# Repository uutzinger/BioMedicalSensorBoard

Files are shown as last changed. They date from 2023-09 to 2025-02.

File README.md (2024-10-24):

# MediBrick

A cost-effective Solution for Biomedical Measurements.

Urs Utzinger, 10/2024 and capstone teams: 24052 (2023/24), 23094 (2022/23).
Biomedical Engineering Department, The University of Arizona.

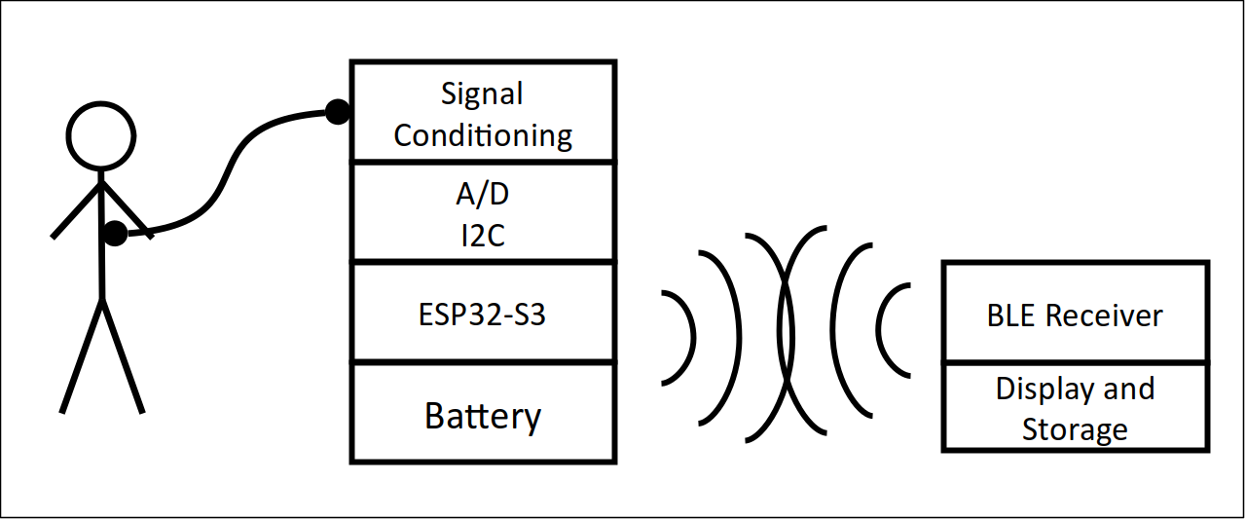
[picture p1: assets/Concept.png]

 
Table of Content:
<!-- TOC start (generated with https://github.com/derlin/bitdowntoc) -->

- [MediBrick](#medibrick)
   * [Problem Description](#problem-description)
   * [Project Goals](#project-goals)
   * [Measurement Solutions](#measurement-solutions)
   * [Microcontroller and Software](#microcontroller-and-software)
   * [Hardware](#hardware)
      + [Design and Manufacturing ](#design-and-manufacturing)
      + [Enclosures](#enclosures)
   * [Project Status](#project-status)

<!-- TOC end -->

<!-- TOC -->

Posters and Papers: 
- *Open source platform to measure physiological signals in a classroom setting*, BMES 2024 Annual Meeting: Biomedical Engineering Education - Poster Session C, Poster Q15 

## Problem Description

Biomedical engineering students need to practice measuring signals from living systems.
Measurement equipment is needed for classroom laboratories that can safely record common physiological parameters.
For a wide adoption, such equipment should be cost effective and repairable in-house.
Therefore, it should take advantage of existing components that are open source and distributed through domestic channels.
While there are commercial systems available [^fn1] [^fn2], there is no unifying approach that takes advantage of existing third party hardware, gives option to expand functionality at later time and uses open source software.  Such measurement modules could also be readily incorporated into academic research projects.

[^fn1]: Bioradio, https://staging.glneurotech.com/product-category/bioradio-all
[^fn2]: Protocentral https://protocentral.com

**An expandable, low-costs, open-design system is needed that measures physiological parameters in a class room setting in a safe manner.**

## Project Goals
- We strive to create an educational system to measure physiological signals.
- It shall be easily manufactured at an educational institution.
- It shall record, display and store common physiological measurements safely in a class room setting.

## Measurement Solutions
This project consists of the following measurement solutions:

| ECG and Impedance | Electronic Stethoscope and Blood Pressure | Pulse Oximeter | Temperature | Inertial Measurement Unit | Air Quality | Lung Capacity |
| --- | --- | --- | --- | --- | --- | --- |
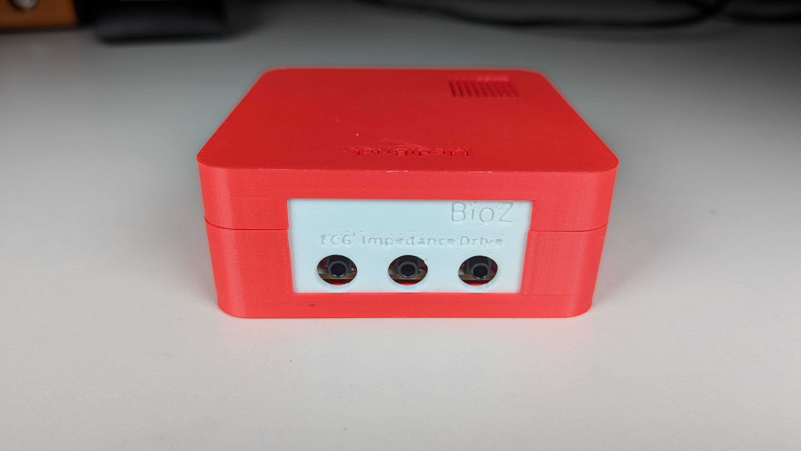
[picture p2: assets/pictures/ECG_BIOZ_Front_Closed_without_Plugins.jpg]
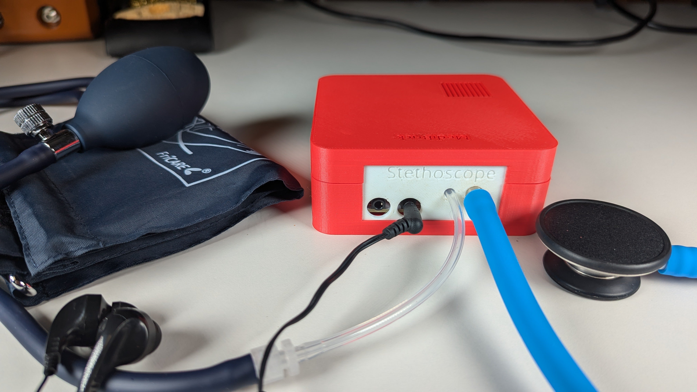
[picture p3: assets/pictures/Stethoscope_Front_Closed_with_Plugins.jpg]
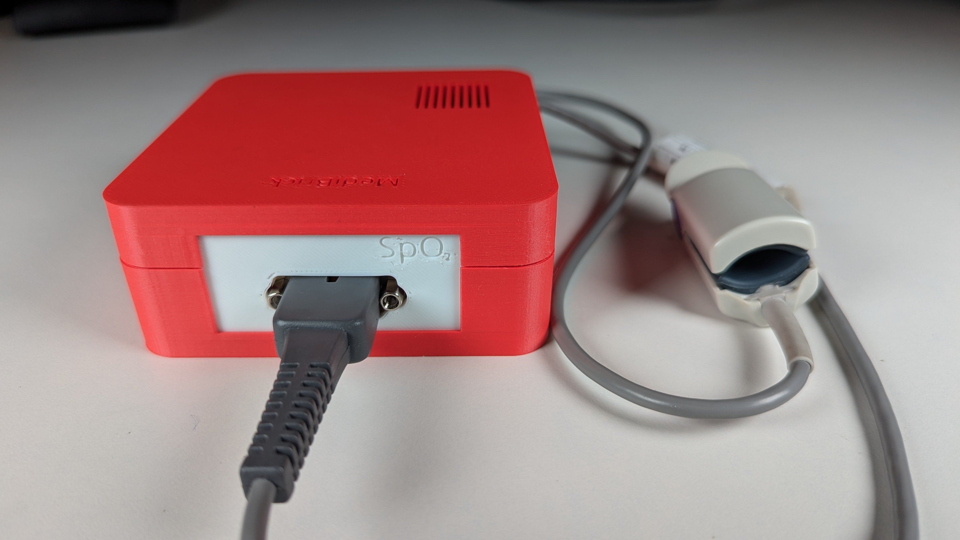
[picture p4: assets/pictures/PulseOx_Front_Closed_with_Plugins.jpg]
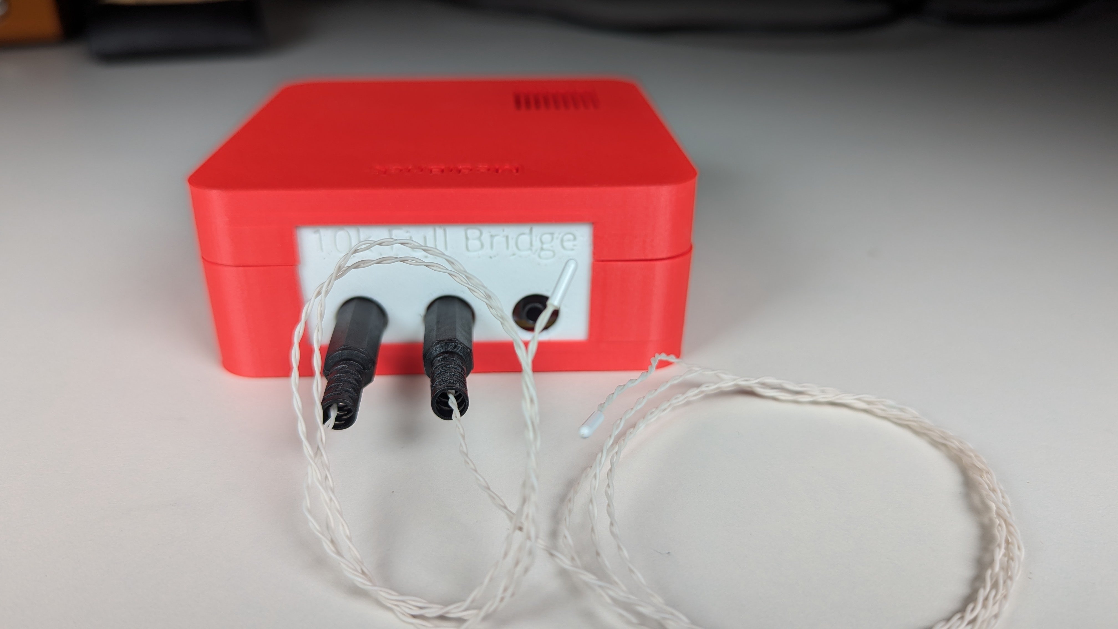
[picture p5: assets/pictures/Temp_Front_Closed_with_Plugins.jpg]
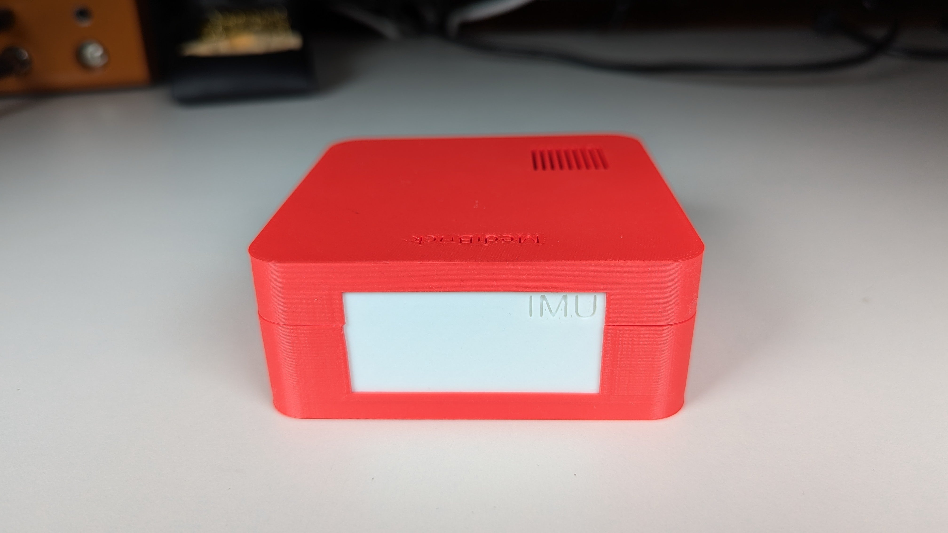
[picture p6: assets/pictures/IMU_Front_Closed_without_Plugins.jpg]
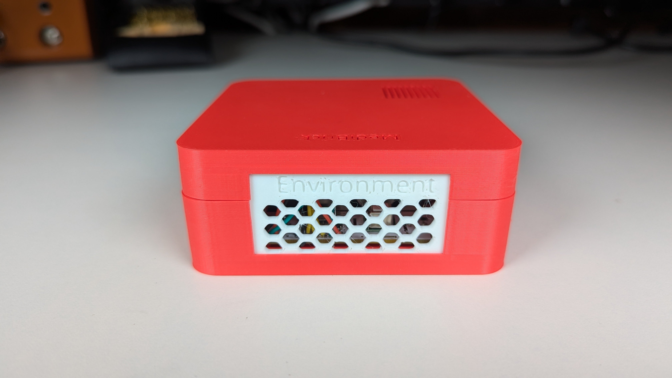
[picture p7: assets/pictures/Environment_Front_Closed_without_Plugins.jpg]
|  |  |  |  |  |  | N.A. |
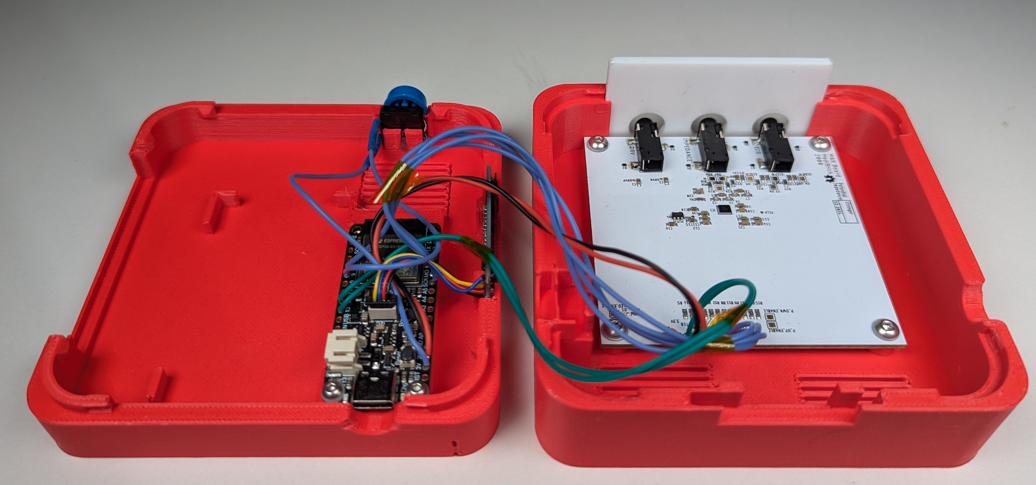
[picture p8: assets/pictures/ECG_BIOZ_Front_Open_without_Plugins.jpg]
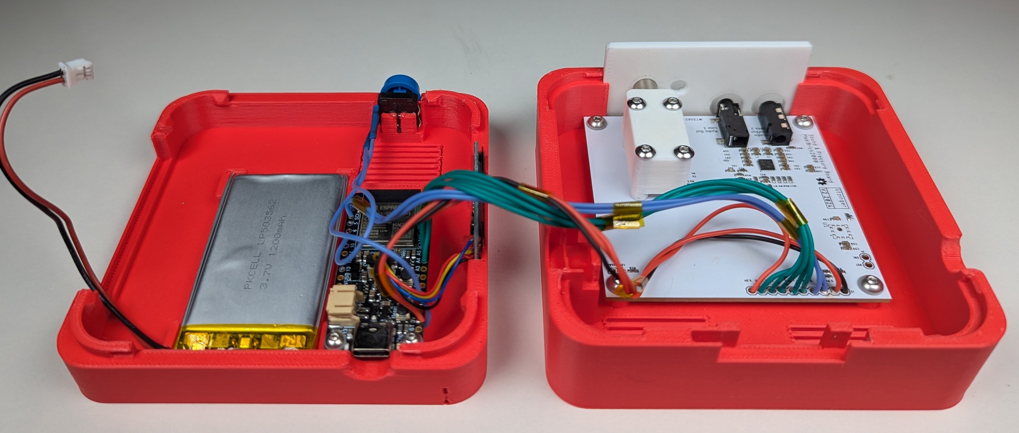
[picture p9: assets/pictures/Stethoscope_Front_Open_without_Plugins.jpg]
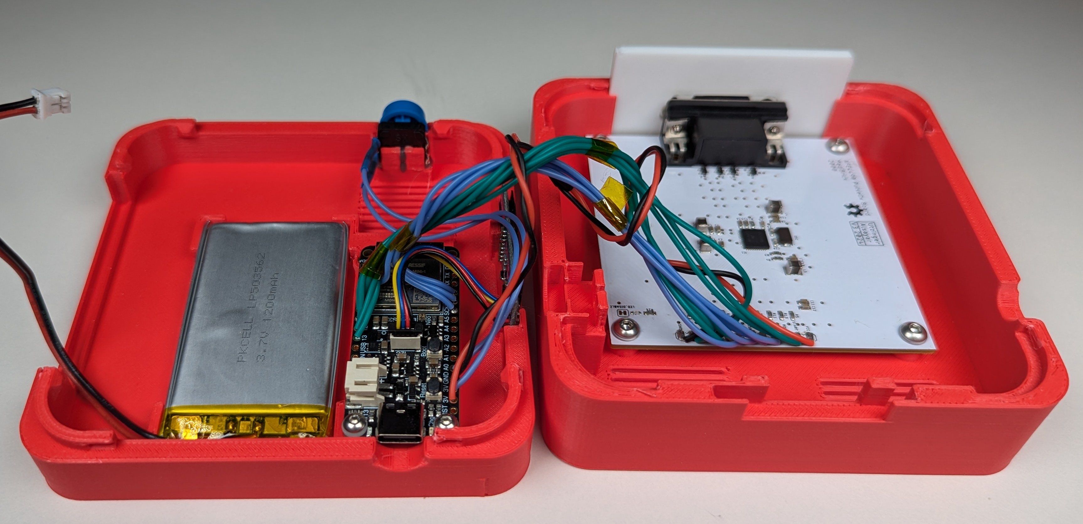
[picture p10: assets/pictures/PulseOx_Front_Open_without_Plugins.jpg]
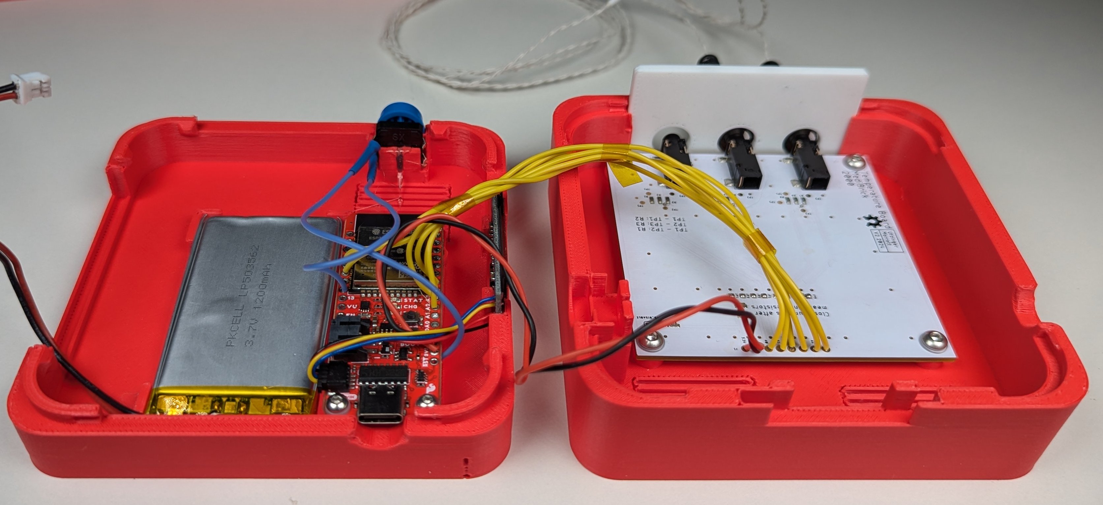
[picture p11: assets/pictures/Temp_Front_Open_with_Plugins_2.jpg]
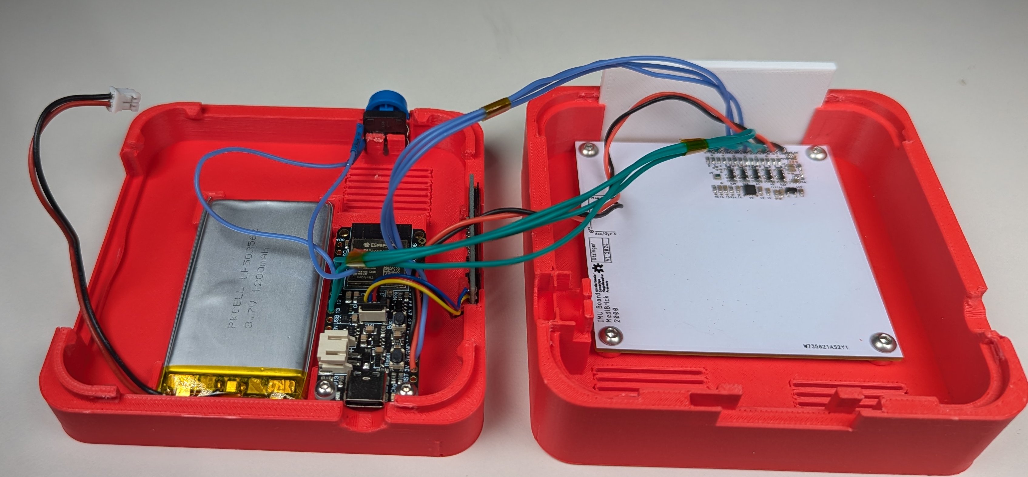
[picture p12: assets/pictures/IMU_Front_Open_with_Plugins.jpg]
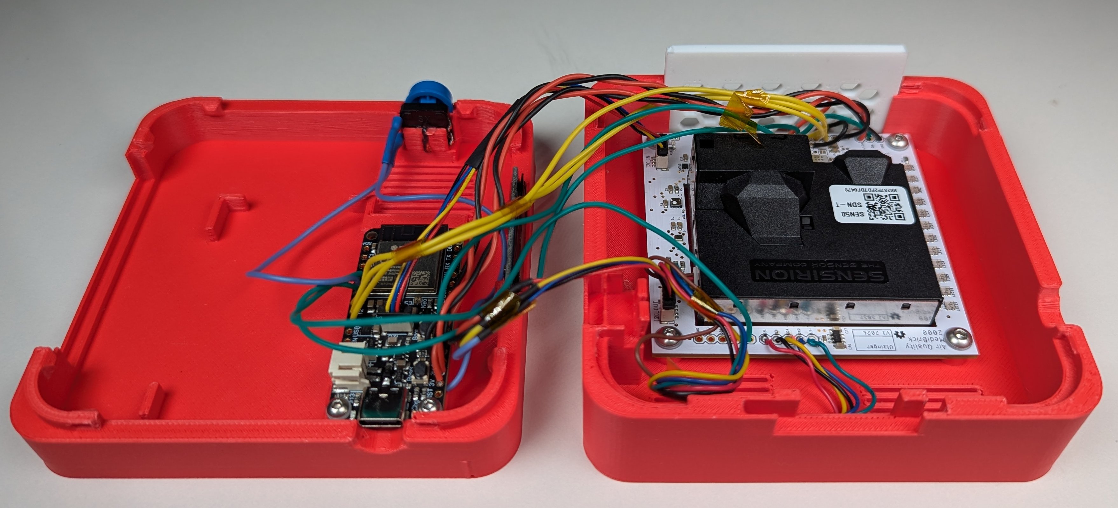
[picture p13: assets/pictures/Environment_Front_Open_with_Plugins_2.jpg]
|  |  |  |  |  |  | N.A. |

Below are the relevant project files. 

Education Content: &#128214;, Sources used to find a solution: &#10004;, Solution: &#128194;, Assembly Instructions: &#128736;, Software: &#128200;

- **General Physiology Background**
    - [Cardiac Physiology](cardiac_physiology.md) &#128214;
    - [Common Physiologic Measurements](physiologic_measurements.md) &#128214;
- **Electro Cardiogram Solutions**
    - [ECG Measurement](ecg_measurements.md) &#128214;
    - [ECG Solutions](ecg_solutions.md) &#10004;
    - [ECG MediBrick v1](ECG_Board/README.md)
    - [ECG MediBrick v2](Impedance_Potential_Board/README.md) based on MAX30001G &#128194;
        - [Assembly Instructions](Impedance_Potential_Board/assembly.md) &#128736;
- **Bio Impedance Solutions**
    - [Impedance Measurement](impedance_measurements.md) &#128214;
    - [Impedance Solutions](impedance_solutions.md) &#10004;
    - [Impedance MediBrick v1](Impedance_Board/README.md) based on AD5933
    - [Impedance MediBrick v2](Impedance_Potential_Board/README.md) based on MAX30001G &#128194;
        - [Assembly Instructions](Impedance_Potential_Board/assembly.md) &#128736;
- **Stethoscope and Sound**
    - [Sound Measurement](sound_measurement.md)&#128214;
    - [Pressure Measurement](pressure_measurements.md) &#128214;
    - [Sound Solutions](sound_solutions.md) Sound Recording Solutions &#10004;
    - [Pressure Solutions](pressure_solutions.md) Pressure Recording Solutions &#10004;
    - [Stethoscope MediBrick V1](Stethoscope_with_3rdparty_Sound/README.md) PCB Artist I2S codec interfacing with ESP
    - [Stethoscope with Blood Pressure MediBrick V2](Stethoscope_with_Pressure/README.md) &#128194;
        - [Assembly Instructions](Stethoscope_with_Pressure/assembly.md) &#128736;
- **Pulse Oximeter**
    - [SpO<sub>2</sub> Measurement](spo2_measurements.md) &#128214;
    - [SpO<sub>2</sub> Solutions](spo2_solutions.md) &#10004;
    - [SpO<sub>2</sub> MediBrick](SPO2_Board/README.md) &#128194;
        - [Assembly Instructions](SPO2_Board/assembly.md) &#128736;
- **Temperature and Strain Gauges**
    - [Temperature Measurement](temperature_measurements.md) &#128214;
    - [Temperature Solutions](temperature_solutions.md) &#10004;
    - [Temperature MediBrick](Thermistor_Board/README.md) &#128194;
        - [Assembly Instructions](Thermistor_Board/assembly.md) &#128736;
- **Acceleration, Gyration, Compass and Pressure Solution**
    - [Activity Measurements with Inertial Measurement Unit](imu_measurements.md)&#128214;
    - [Inertial Measurement Unit Solutions](imu_solutions.md) &#10004;
    - [IMU MediBrick](IMU_Board/README.md)&#128194;
        - [Assembly Instructions](IMU_Board/assembly.md) &#128736;
    - IMU MediBrick v2. Not available yet, but should include Real Time Kinematic GPS such as [ZED-F9P](https://www.u-blox.com/en/product/zed-f9p-module)
- **Air Quality**
    - [Airquality Measurement](airquality_measurements.md)&#128214;
    - [Airquality Solutions](airquality_solutions.md) &#10004;
    - [Airquality MediBrick](Airquality/README.md) &#128194;
        - [Assembly Instructions](Airquality/assembly.md) &#128736;
- **Lung Capacity**
    - Not available yet, will be based on Sensirion [SFM3304-D](https://sensirion.com/products/catalog/SFM3304-D)

## Microcontroller and Software

- [Software and Programming](microcontroller_programming.md) 
- [Microcontroller Options](microcontroller_solutions.md)

To visualize data I recommend [SerialUI](https://github.com/uutzinger/SerialUI) &#128200;

## Hardware

### Design and Manufacturing 

- [Mechanical Parts Manufacturing](mechanical_design_and_manufacturing.md): Approach to convert the mechanical models to 3D printing instructions.
- [PCB Design](electronic_design.md): Settings for Eagle CAD.
- [PCB Manufacturing](pcb_manufacturing.md): Settings for PCBWay.

### Enclosures
| Assembly| Top | Bottom |
| ------- | ------ |  ------ |
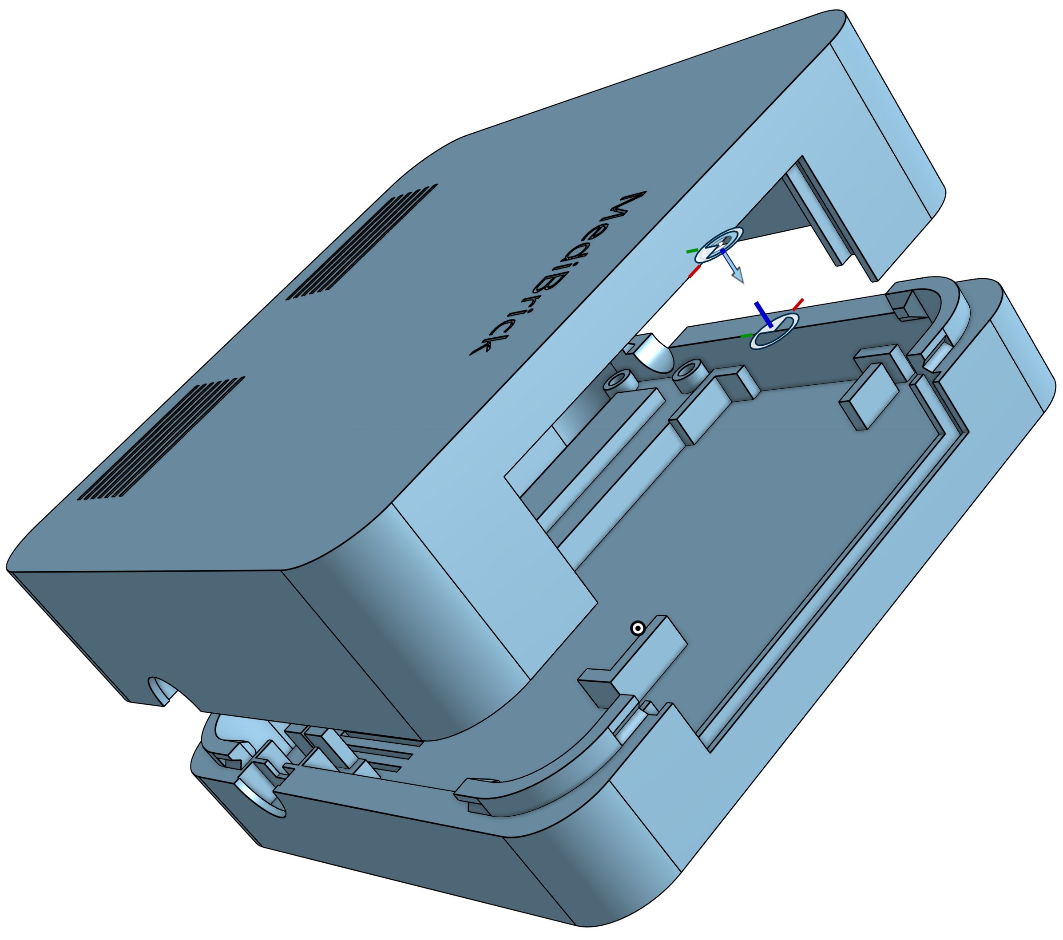
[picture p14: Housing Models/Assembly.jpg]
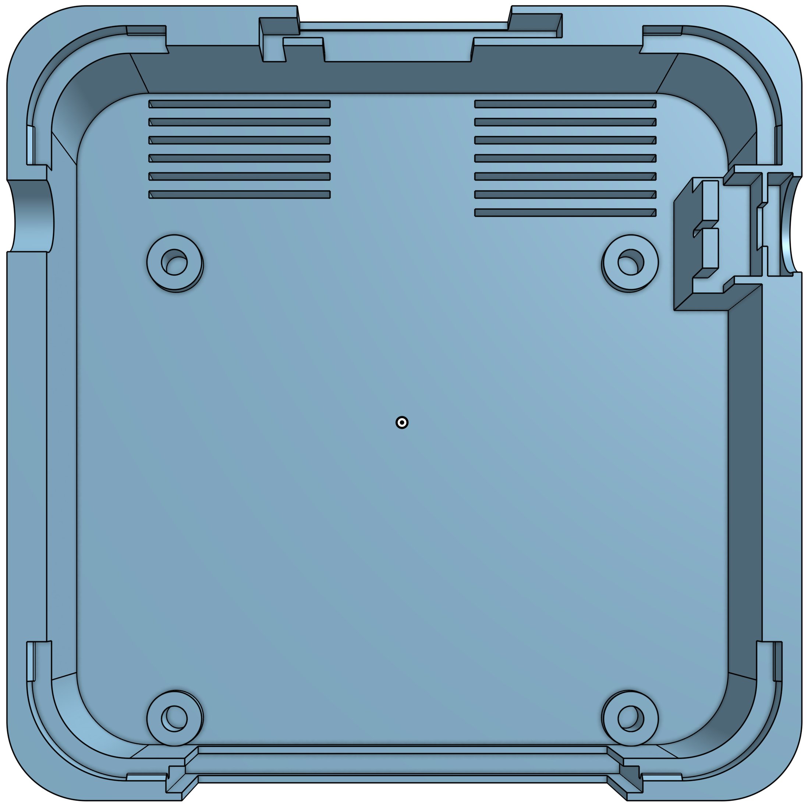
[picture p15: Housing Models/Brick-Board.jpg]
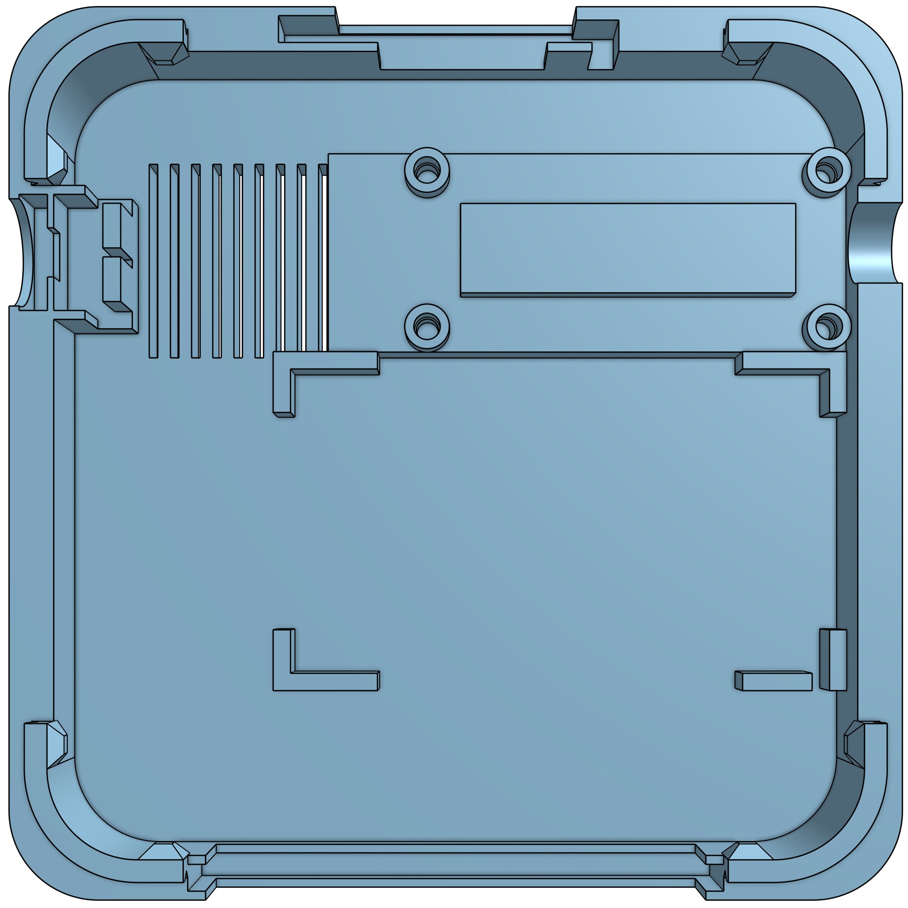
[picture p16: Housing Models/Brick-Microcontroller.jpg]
|  |  |  |

Receiver

Charging Station

## Project Status

| Brick | Mechanical CAD | Electrical CAD|  Assembled | Test Software | Production Software
| ------- | ------ |  ------ | ------ | ------ | ------ |
| **Temperature**     | Completed | Completed | Completed | Completed | Working on |
| **SpO<sub>2</sub>** | Completed | Completed | Completed | Completed| Working on
| **Stethoscope**     | Completed | Testing   | Testing   | Sound Optimizing, Pressure Testing | Working on
| **Air Quality**     | Completed | Completed| Completed | MICS sensor support missing | Working on
| **IMU**             | Completed | Completed | Completed | Completed | Working on
| **Bio Potential and BIOZ** | Completed | Untested | Untested | Driver incomplete | Working on
| Protoype Sound w third arty ES8388 | Completed | Completed | Completed | Completed | N.A. |  
| Impedance w AD 5933 network analyzer | Completed | Optimization | Testing| Incomplete | N.A.|
| ECG w Sparkfun Breakout | Completed | Completed | Completed | Completed | N.A. |
| Thermistor/Strain Gauge board using LTC2473 | Completed | Completed | Completed | Completed | N.A. |

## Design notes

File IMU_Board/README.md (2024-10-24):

# IMU MediBrick

<a href="../assets/pictures/IMU_Front_Closed_without_Plugins.jpg" target="_blank" >
  
</a>

This board is based on latest TDK IMU [ICM20948](datasheest/DS-000189-ICM-20948-v1.3.pdf) and BOSCH precision pressure sensors [BMP581](datasheets/BSS138-D.pdf) and uses SPI interface accommodating a sampling rate exceeding 1000 samples per second.

## Costs &#36;

| Item        | Quantity at Purchase | Costs  | Source            | Cost per Brick
|---                          | ---  | ---    | ---               | ---
| Microcontroller             |  1   | $17.5  | [Adafruit](https://www.adafruit.com/product/5477)          | $17.5
| Display                     |  5   | $13    | [Amazon](https://a.co/d/1QH0Ab9)            | $3
| Button                      | 25   | $9     | [Amazon](https://a.co/d/8KAuTwC) | $0.5 
| Battery                     |  1   | $10     | [Adafruit](https://www.adafruit.com/product/258)        | $10
| PCB                         |  5   | $45.20  | PCBWay            | $9
| Parts and Assembly          |  2   | $51.87* | PCBWay            | $26
| Assorted Wires              |8m    | $15    | [Amazon](https://a.co/d/58djefc) | $1
| Assorted Screws and Nuts    |100   |  $7    | Amazon            | $0.05
| Assorted 3D printed parts   |      |        |  | $3
|                             |      |        |                   |
| **Total**                   |      |        |                   | **$70**

*Electronic components are $11 per board. 

## Test Software &#128187;
Test software is located in the Arduino folder.

| Folder | Description | 
|--- |---|
|MediBrick_IMU_ICM20948_DMP_Test | IMU with onboard attitude calculation. |
|MediBrick_IMU_P_BMP581_Interrupt| Pressure sensor with interrupt. |

## Microcontroller Software : &#9000;
Not finalized yet

## Electronics Design &#128268;

<a href="IMU_schematic.pdf" target="_blank">
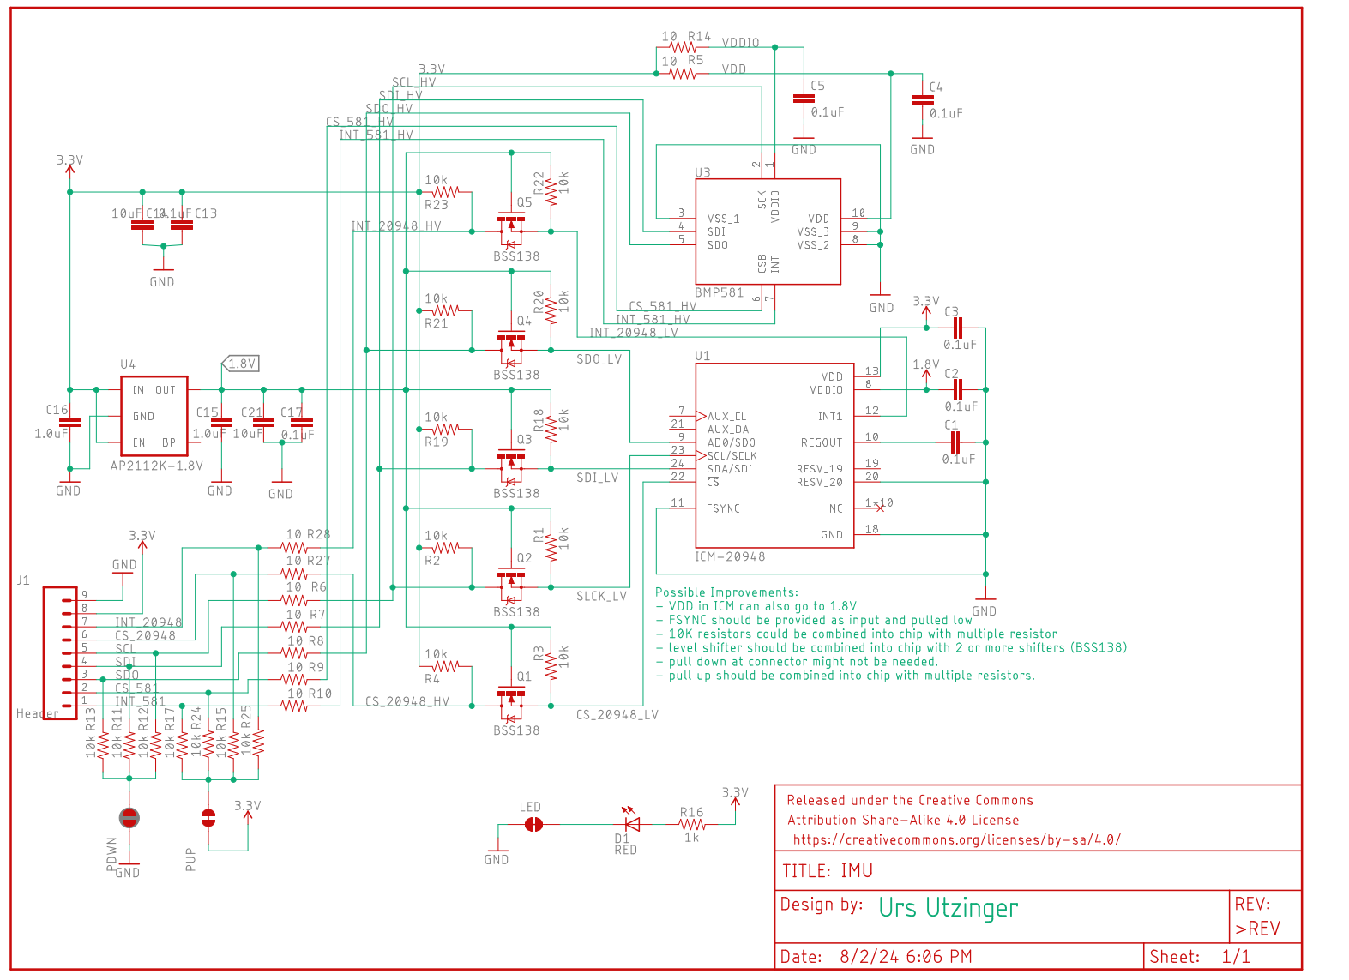
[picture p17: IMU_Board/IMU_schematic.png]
  
</a>

<a href="IMU_board.pdf" target="_blank">
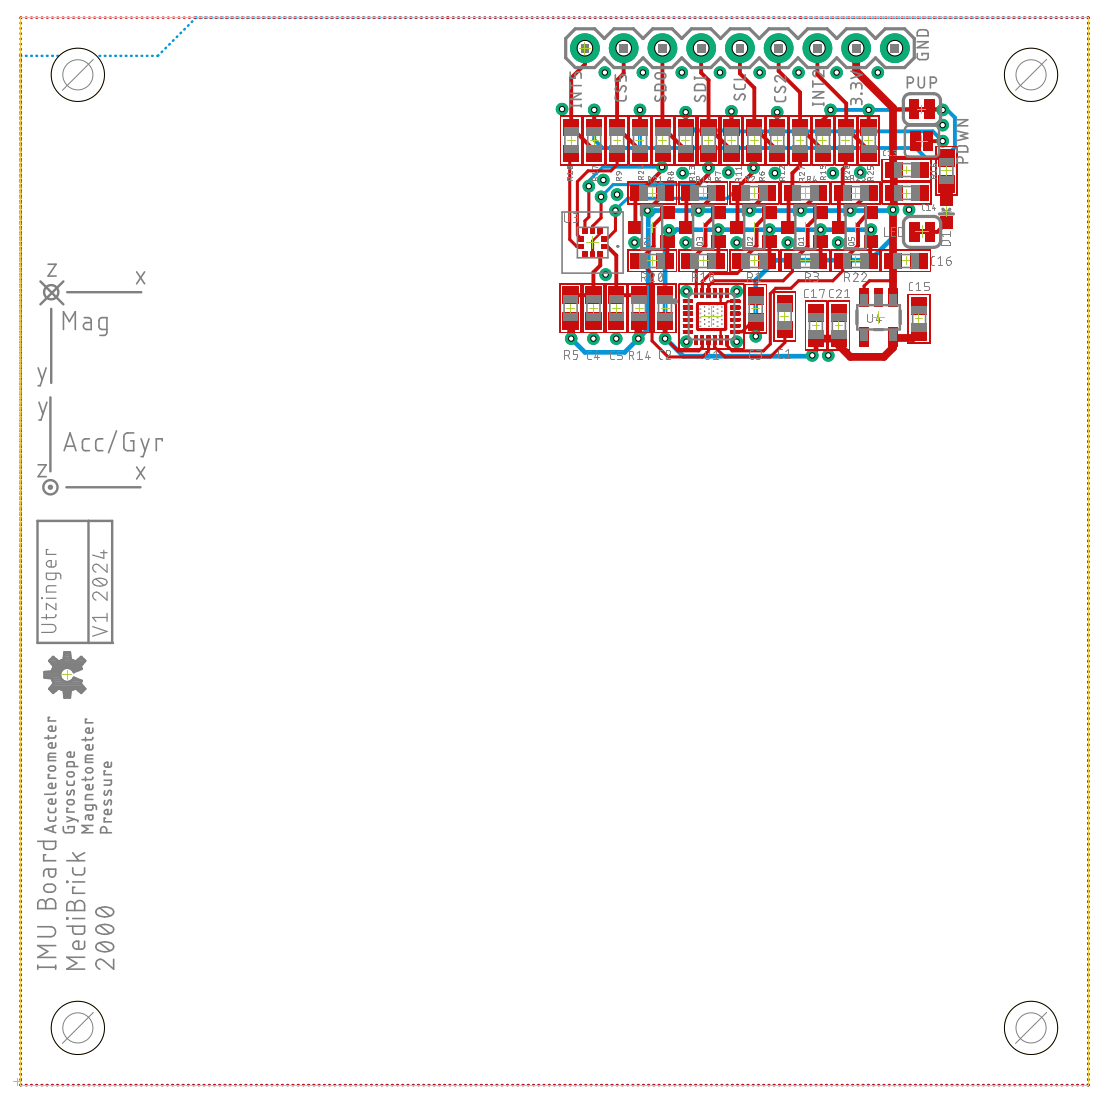
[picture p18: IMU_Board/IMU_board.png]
  
</a>

The following files are needed for PCB manufacturing and assembly.

- [Bill of Materials](IMU_BOM.xlsx)
- [Manufacturing Files](IMU_2024-08-03.zip)
- [Pick and Place](IMU_PnP.xlsx)

The Bill of Materials is formatted so that its compatible with PCBWay submissions.

## 3D Printed Parts &#9881;
These are the links to the OnShape Design files, which you can edit and modify if you have an OnShape account (OnShape has free academic accounts).

- Medi Brick
  - [Brick Top](https://cad.onshape.com/documents/be6b7e5f847d89f3ec5eb9d5/w/761fee9865ca7ef709028476/e/ff897b4f359cec83b782ff14)
  - [Brick Bottom](https://cad.onshape.com/documents/92ad78475e8f0b17ff5e260b/w/88a02abbcb12cdbd4d9de3ad/e/fb79ca58ad2b6a0298e9d1b6)
  - [Brick Assembly](https://cad.onshape.com/documents/11cbfe9c3c739b6e8ecbf3d7/w/989b564ecd7f6d069e643ac0/e/85542f706be8cc7554218e8d)
  - [IMU Brick Side Plate](https://cad.onshape.com/documents/eb58e78174fdb2053487973b/w/903e17c4126fb90e8782ab92/e/f4b50a954b0de64bf397a15c?renderMode=0&uiState=6712e42015dc976491f468b3)

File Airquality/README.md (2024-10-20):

# Airquality

<a href="..\assets\pictures\Environment_Front_Closed_without_Plugins.jpg" target="_blank">
  
</a>

The airquality solution uses several sensors:

| Measurand | Sensors | Manufacturer | approx. Cost |
|---        |---      | ---          | ---  |
| Particulate Matter | Sensirion | [SEN50](datasheets/Sensirion_Datasheet_Environmental_Node_SEN5x.pdf) |  $22.20 |
| CO<sub>2</sub>               | Sensirion | [SCD40](datasheets/SCD4x_Ver1.4_Feb2023.pdf)| $29.70 |
| relative Humidity and Temperature |  Sensirion | [SHT45](datasheets/Datasheet_SHT4x_1.pdf) | $6.40|
| barometric Pressure | Bosch | [BMP581](datasheets\bst_bmp581_ds004-2950309.pdf)| $4.20 |
| eVOC, eNOX | Sensirion | [SGP41](datasheets\Sensirion_Gas_Sensors_Datasheet_SGP41.pdf) | $9 |
| Carbon Monoxide, Amonia, Nitrogenoxide | Amphenol SGX Sensortech | [MiCS-6814 MEMS]((datasheets\1143_Datasheet-MiCS-6814-rev-8,pdf)) | $17 |
| Status Lights | XING Light | [Neopixel](datasheets\2301111010_XINGLIGHT-XL-2020RGBC-WS2812B_C5349955.pdf)| |

The MiCS sensor does not have an integrated analog to digital conversion and the device is measured with a resistor network. The datasheet shows operation at 5V. In this [document](MICS6814_on_3V.md) the calculations and illustration for the MiSC operating at 3V is explained. The nominal resistor values vary greatly and the detector needs tuning.

## Costs &#36;

| Item        | Quantity at Purchase | Costs  | Source            | Cost per Brick
|---                          | ---  | ---    | ---               | ---
| Microcontroller             |  1   | $17.5  | [Adafruit](https://www.adafruit.com/product/5477)          | $17.5
| Display                     |  5   | $13    | [Amazon](https://a.co/d/1QH0Ab9)            | $3
| Button                      | 25   | $9     | [Amazon](https://a.co/d/8KAuTwC) | $0.5 
| Battery                     |  1   | $10     | [Adafruit](https://www.adafruit.com/product/258)        | $10
| PCB                         |  5   | $45.20  | PCBWay            | $9
| Parts and Assembly          |  2   | $216.96 | PCBWay            | $109
| SEN50                       |  1   | $22.20  | [Mouser](https://www.mouser.com/ProductDetail/Sensirion/SEN50-SDN-T?qs=MyNHzdoqoQK%2F9NY8sYsxtw%3D%3D) | $22.20
| QWIIC cable                 |  1   | $1     | [Adafruit](https://www.adafruit.com/product/4210) | $1 |
| SEN5x cable                 | 1    | $1.50  | [Sparkfun](https://www.sparkfun.com/products/18079) | $1.50 
| Assorted Wires              |8m    | $15    | [Amazon](https://a.co/d/58djefc) | $1
| Assorted Screws and Nuts    |100   |  $7    | Amazon            | $0.05
| Assorted 3D printed parts   |      |        |                   | $3
|                             |      |        |                   |
| **Total**                   |      |        |                   | **$180**

*Electronic components excluding SEN50 are $128 per board. 

The airquality solution has been optimized for accuracy and not cost. There are sensor options for half or third of the price but they require a different board design.

## Test Software &#128187;
Test software is located in the Arduino folder.

| Folder | Description | 
|--- |---|
| MediBrick_Env_CO2_SCD4x           | CO2 sensor test             |
| MediBrick_Env_Humidity_SHT_Test   | Humidity and Temperature test |
| MediBrick_Env_PM_SEN5x_Test       | Particulate Matter test     |
| MediBrick_Env_VOC_NOx_SGP41_Test  | eVOC and NOx test           |
| MediBrick_Env_NeoPixel_Test       | RGB LED indicator test      |
| Not yet available                 | MiCS CO, Amonia Sensor, NOx test | 
## Microcontroller Software : &#9000;
An integrative software reading all sensors is not finalized yet.

## Electronics Design &#128268;

<a href="Airquality_schematic.pdf" target="_blank">
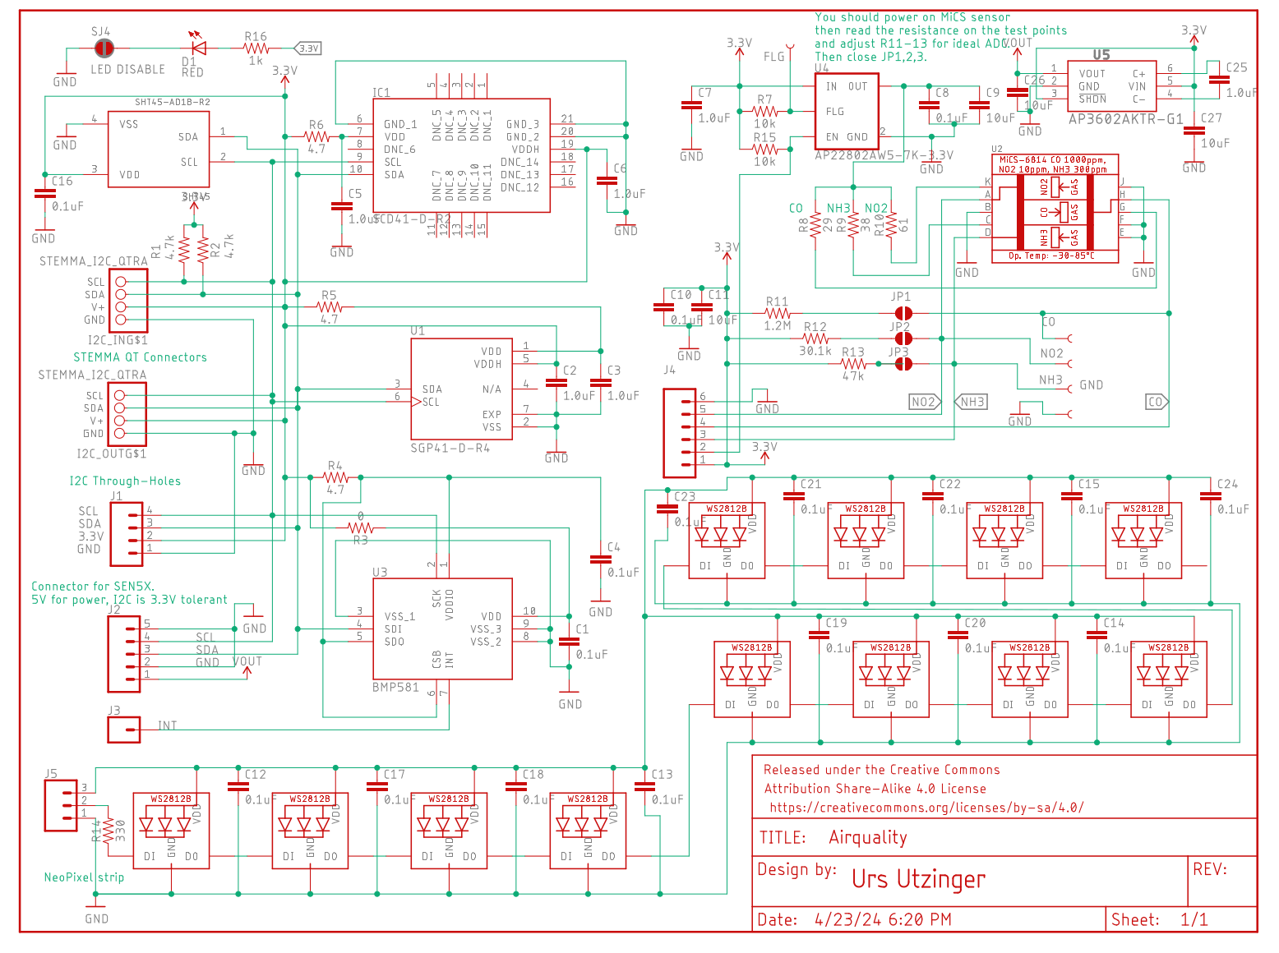
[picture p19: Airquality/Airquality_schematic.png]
  
</a>
<a href="Airquality_board.pdf" target="_blank">
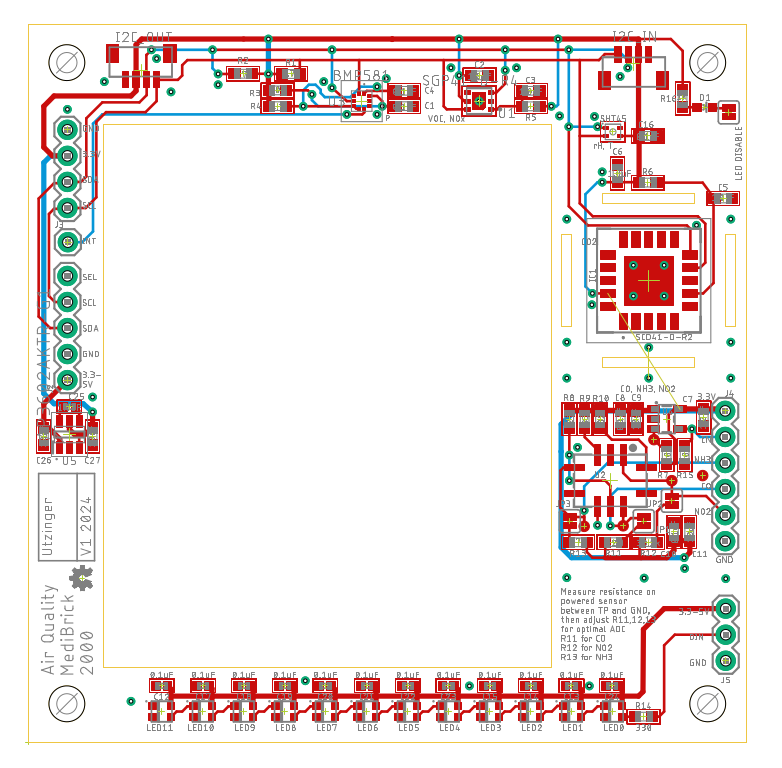
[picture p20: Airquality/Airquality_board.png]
  
</a>

The particulate matter sensor is placed in the middle of the PCB and should not touch the PCB to avoid vibrations on the CO<sub>2</sub> sensor.

The following files are needed for PCB manufacturing and assembly.

- [Bill of Materials](Air_Quality_BOM.xlsx)
- [Manufacturing Files](Air_Quality_2024-08-24.zip)
- [Pick and Place](Air_Quality_PnP.xlsx)

The Bill of Materials is formatted so that its compatible with PCBWay submissions.

## 3D Printed Parts &#9881;
These are the links to the OnShape Design files, which you can edit and modify if you have an OnShape account (OnShape has free academic accounts).

- Medi Brick
  - [Brick Top](https://cad.onshape.com/documents/be6b7e5f847d89f3ec5eb9d5/w/761fee9865ca7ef709028476/e/ff897b4f359cec83b782ff14)
  - [Brick Bottom](https://cad.onshape.com/documents/92ad78475e8f0b17ff5e260b/w/88a02abbcb12cdbd4d9de3ad/e/fb79ca58ad2b6a0298e9d1b6)
  - [Brick Assembly](https://cad.onshape.com/documents/11cbfe9c3c739b6e8ecbf3d7/w/989b564ecd7f6d069e643ac0/e/85542f706be8cc7554218e8d)
  - [Air Quality Brick Side Plate](https://cad.onshape.com/documents/6f9a87cae125641fc3a0651c/w/6e25f32c6ac446efd4e51be7/e/7a2fa3c5e053c8442ada89bd)

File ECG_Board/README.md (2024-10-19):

This is a description for ECG Sensor from the capstone project: https://github.com/grender007/Modular-Biomedical-Sensor-Board-for-Education

The ECG Module takes advantage of the Sparkfun ECG Pre-Amplifier Board. It uses the AD8232 IC to detect the voltage potential of the heart. 
The microcontroller's analog to digital converter is needed to record the signal.

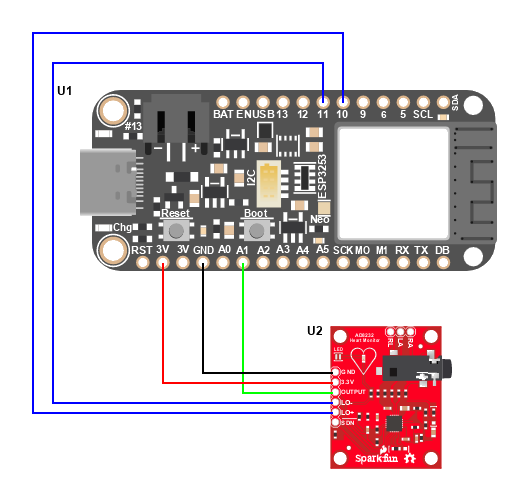
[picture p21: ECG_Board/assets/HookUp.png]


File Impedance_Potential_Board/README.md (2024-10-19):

# Bio Impedance and Bio Potential

<a href="..\assets\pictures\ECG_BIOZ_Front_Closed_without_Plugins.jpg" target="_blank" style="float: right; margin-left: 20px;">
  
</a>

In the BIOZ and ECG MediBrick we use the MAXIM [MAX30001G](datasheets/max30001g.pdf) analog front end (AFE). It's a modern IC with a "waver level packaging" foot print which makes is difficult to solder and requires precise PCB manufacturing.

The MAX30001G can measure:

- Biopotential
  - ECG (waveform)
  - R-R Time (heart rate and heart rate variability)
- Bioimpedance
  - Resp (respiration rate)
  - GSR (galvanic skin response, stress level)
  - EDA (electro dermal activity)

Here [MAX3001G](MAX30001G.md) we summary capabilities from the datasheet.

For general consideration of bio impedance design and safety: [Analog Devices: Bio-Impedance Circuit Design for Body Worn Systems"](https://www.analog.com/en/resources/analog-dialogue/articles/bioimpedance-circuit-design-challenges.html)

## Costs &#36;

| Item        | Quantity at Purchase | Costs  | Source            | Cost per Brick
|---                          | ---  | ---    | ---               | ---
| Microcontroller             |  1   | $17.5  | [Adafruit](https://www.adafruit.com/product/5477)          | $17.5
| Display                     |  5   | $13    | [Amazon](https://a.co/d/1QH0Ab9)            | $3
| Button                      | 25   | $9     | [Amazon](https://a.co/d/8KAuTwC) | $0.5 
| Battery                     |  1   | $10     | [Adafruit](https://www.adafruit.com/product/258)        | $10
| PCB                         |  5   | $145.80 | PCBWay            | $29
| Parts and Assembly          |  5   | $186.42 | PCBWay            | $38
| Assorted Wires              |8m    | $15    | [Amazon](https://a.co/d/58djefc) | $1
| Assorted Screws and Nuts    |100   |  $7    | Amazon            | $0.05
| Assorted 3D printed parts   |      |        |                   | $3
| ECG 3.5mm cables | 1  | $5.50 | [Sparkfun](https://www.sparkfun.com/products/12970) | $5.50
| Electrodes (consumable) | 100 | $25 | [Amazon](https://a.co/d/85M2rC2) | $ 1
|                             |      |        |                   |
| **Total**                   |      |        |                   | **$110**

Electronic components are $20 per board. Because of WLP foot print of MAX30001G the PCB is 3 times as expensive as the other PCBs.

## Test Software &#128187;
Test software is located in the Arduino folder.

| Folder | Description | 
|--- |---|
| MAX30001G Driver | under development |
| Test programs    | not available yet |

## Microcontroller Software : &#9000;
Not available yet.

## Electronics Design &#128268;

<a href="Impedance_Potential_schematic.pdf" target="_blank">
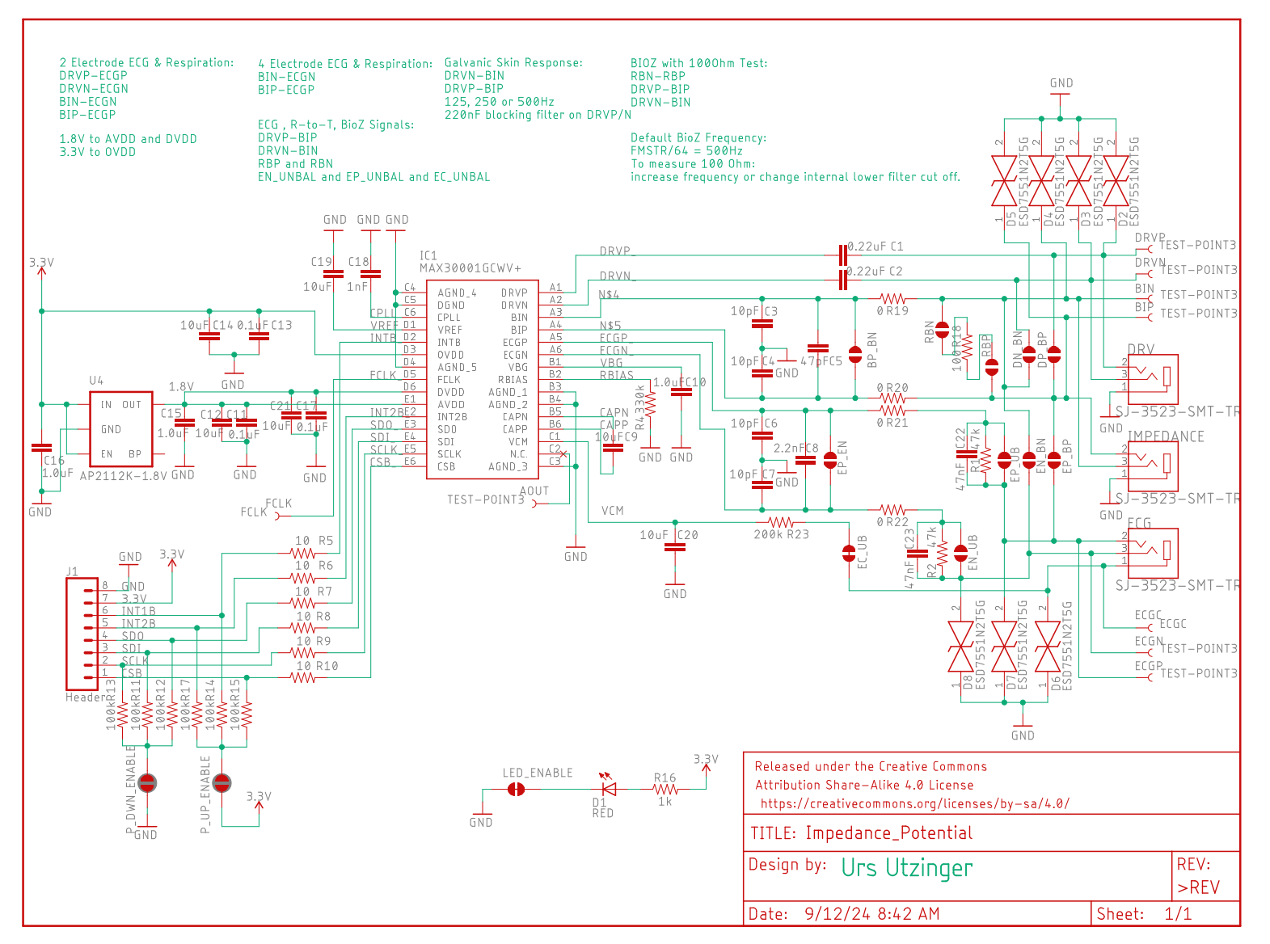
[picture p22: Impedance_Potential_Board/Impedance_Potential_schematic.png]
  
</a>
<a href="Impedance_Potential_board.pdf" target="_blank">
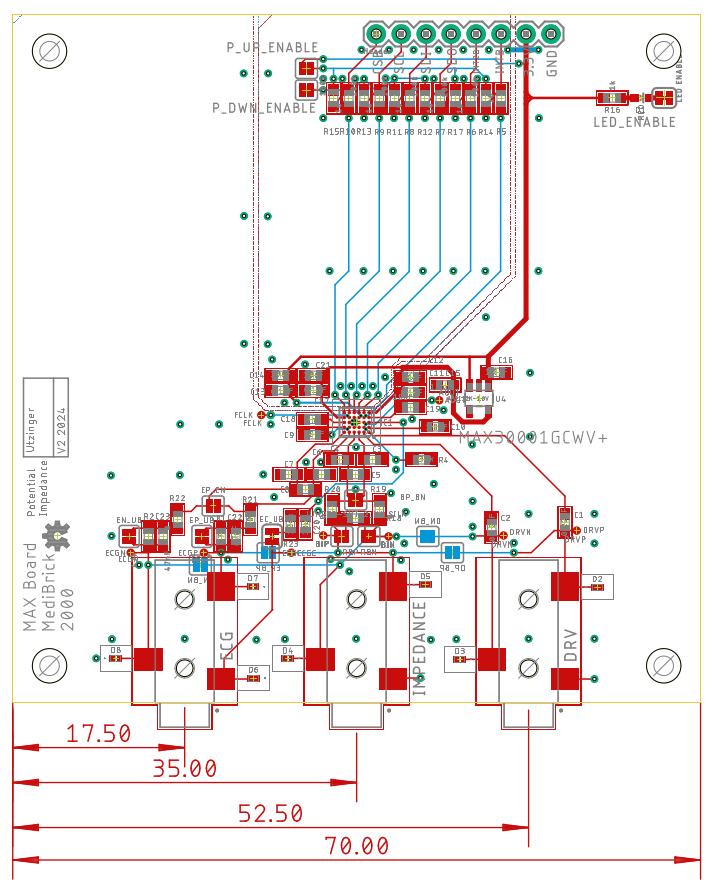
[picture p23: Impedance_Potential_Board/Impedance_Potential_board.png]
  
</a>

The following files are needed for PCB manufacturing and assembly.

- [Bill of Materials](Impedance_Potential_BOM.xlsx)
- [Manufacturing Files](Impedance_Potential_2024-09-12.zip)
- [Pick and Place](Impedance_Potential_PnP.xlsx)

The Bill of Materials is formatted so that its compatible with PCBWay submissions.

## 3D Printed Parts &#9881;
These are the links to the OnShape Design files, which you can edit and modify if you have an OnShape account (OnShape has free academic accounts).

- Medi Brick
  - [Brick Top](https://cad.onshape.com/documents/be6b7e5f847d89f3ec5eb9d5/w/761fee9865ca7ef709028476/e/ff897b4f359cec83b782ff14)
  - [Brick Bottom](https://cad.onshape.com/documents/92ad78475e8f0b17ff5e260b/w/88a02abbcb12cdbd4d9de3ad/e/fb79ca58ad2b6a0298e9d1b6)
  - [Brick Assembly](https://cad.onshape.com/documents/11cbfe9c3c739b6e8ecbf3d7/w/989b564ecd7f6d069e643ac0/e/85542f706be8cc7554218e8d)
  - [Impedance Potential Plate](https://cad.onshape.com/documents/4b23bdc1fe41aa5490b46d9c/w/fd4737f6a1ca7fbcd3b1d7f7/e/89122d5ddac798ebf451ad60)

## MAX30001G Design

## Block Diagram of MAX 30001G

<a href="assets/Blockdiagram.png" target="_blank">
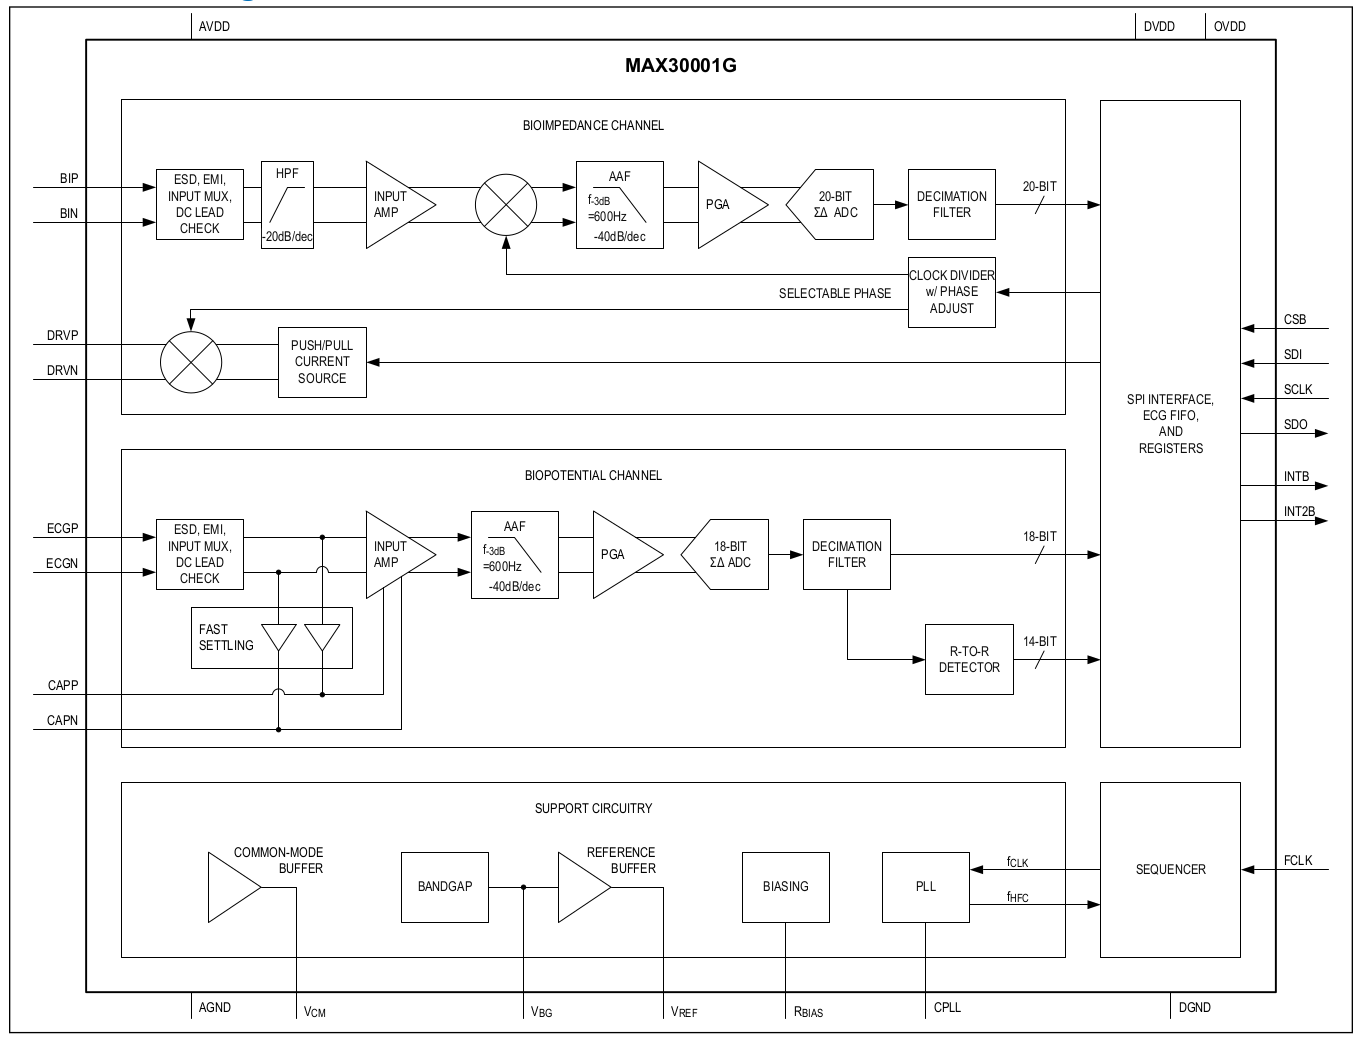
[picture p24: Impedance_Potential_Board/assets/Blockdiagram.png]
  
</a>

## External Configuration Options

<a href="Design.svg" target="_blank">
  
</a>

We have the following external connectors:
- ECG, 3,5mm audio
    - ECG_N (middle of plug) e.g. left arm
    - ECG_P (proximal side of plug) e.g. right arm
    - VCM/ECG_GND (common mode) (tip of plug) e.g. leg

- Impedance, 3.5mm audio
    - BI_N
    - BI_P
    - GND (tip of plug)

- Driver, 3.5mm audio
    - DRV_P
    - DRV_N
    - GND (tip of plug)

### Options
- We can operate the board to measure ECG or Impedance or both. 
- We can operate the board to use only two leads, four leads or six leads. 
    - 6 leads ECG on ECGP & ECGN, BIOZ on BINP & BINN and DRV on DRVP & DRVN
    - 4 leads ECG on ECGP & ECGN, BIOZ on BINP & BINN
    - 2 leads ECG, BIOZ, DRV on ECGP & ECGN
- We can configure the board to measure impedance of a calibration resistor that is soldered onto the board (100 Ohm).

### Component Values

Typical values and conditions of external components

Name      | typical value | Comment
----------|---------------|--------
C_ECG     | 2.2nF         | datasheet
C_ECG-G   | 10pF          | datasheet, 47pF protocentral
EP_EN     | open          | if closed disable ECG
R_ECG     | 0,51k,200k Ohm | 0, 200k shown in datasheet (200k when ECG conencted with BIOZ), 51k protocentral, 0 Ohm evaluation kit
R_ECG-B   | 51k           | evaluation kit
C_ECG_B   | 47nF          | evaluation kit
ECG_UNBAL | open          | if closed disable balancing
||
EP_BP     | open          | impedance and ECG is on different plug
EN_BN     | open          | impedance and ECG is on different plug
||
C_BIN     | 47pF          | datasheet
C_BIN_G   | 10pF          | datasheet
BP_BN     | open          | if closed disable BioZ
R_BIN     | 0, 200 Ohm    | 200 protocentral where ECG is connected to BIN, 0 evaluation kit
R_CAL     | 100 Ohm       | evaluation kit
RP        | open          | if closed no external impedance
RN        | open          | "
||
BP_DP     | open          | impedance and driver on different plug
BN_DN     | open          | impedance and driver on different plug
||
C_DRV     | 200nF, 47nF   | 47nF protocentral, 47nF evaluation kit
||
R_VCM     | 0 Ohm,10k,200k| 10k protocentral, evaluation kit has buffer driver circuit, 200k datasheet
R_VCM-B   | 51k, none     | none protocentral & evaluation kit
C_VCM-B   | 47nF, none    | none protocentral & evaluation kit, 47nF datasheet
VMC_UNBAL | open          |

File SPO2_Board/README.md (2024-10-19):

# Pulse Oximeter 

<a href="../assets/pictures/PulseOx_Front_Closed_with_Plugins.jpg" target="_blank" >
  
</a>

This pulesoximeter solution is based on Texas Instruments [AFE4490](datasheets/afe4490.pdf) This is a dual wavelelength pulseoximeter driver that interfaces DB9 connector based Nellcor OxiMax SpO2 Sensor.

## Costs &#36;

| Item        | Quantity at Purchase | Costs  | Source            | Cost per Brick
|---                          | ---  | ---    | ---               | ---
| Microcontroller             |  1   | $17.5  | [Adafruit](https://www.adafruit.com/product/5477)          | $17.5
| Display                     |  5   | $13    | [Amazon](https://a.co/d/1QH0Ab9)            | $3
| Button                      | 25   | $9     | [Amazon](https://a.co/d/8KAuTwC) | $0.5 
| Battery                     |  1   | $10     | [Adafruit](https://www.adafruit.com/product/258)        | $10
| PCB                         |  5   | $45.20  | PCBWay            | $9
| Parts and Assembly          |  2   | $54*    | PCBWay            | $29
| DB9 Connector               |  1   | $2.40** | [Mouser](https://www.mouser.com/ProductDetail/TE-Connectivity-AMP/2301843-1?qs=rrS6PyfT74crws9wAQVNoA%3D%3D) | $2.40
| Nellcor OxiMax SpO2         |  1   | $14.30    | [Biometric Cables](https://www.biometriccables.in/collections/short-spo2-sensors/products/nellcor-oximax-compatible-short-spo2-sensor-adult) | $14.30
| Assorted Wires              |8m    | $15    | [Amazon](https://a.co/d/58djefc) | $1
| Assorted Screws and Nuts    |100   |  $7    | Amazon            | $0.05
| Assorted 3D printed parts   |      |        |                   | $3
|                             |      |        |                   |
| **Total**                   |      |        |                   | **$90**

*Electronic components without DB9 connecter are $12 per board. 

**The DB9 connector was soldered on manually after receiving the populated board.

## Test Software &#128187;
Test software is located in the Arduino folder.

| Folder | Description | 
|--- |---|
|MediBrick_PulseOx_AFE44XX_Test | Comprehensive program that can change all device settings during runtime. |

## Microcontroller Software : &#9000;
Not finalized yet

## Electronics Design &#128268;

<a href="PulseOxi_schematic.pdf" target="_blank">
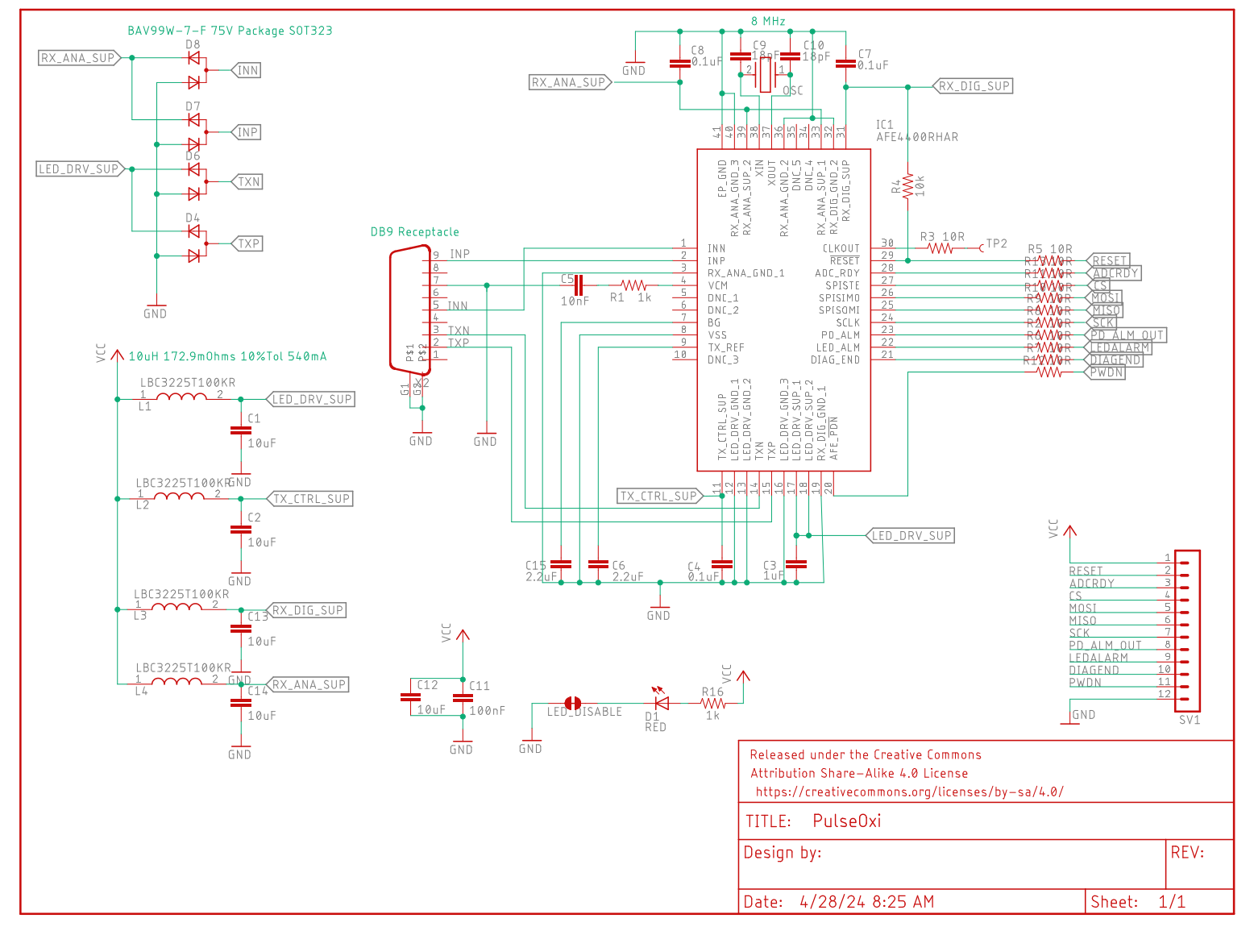
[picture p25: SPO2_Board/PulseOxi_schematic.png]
  
</a>
<a href="PulseOxi_board.pdf" target="_blank">
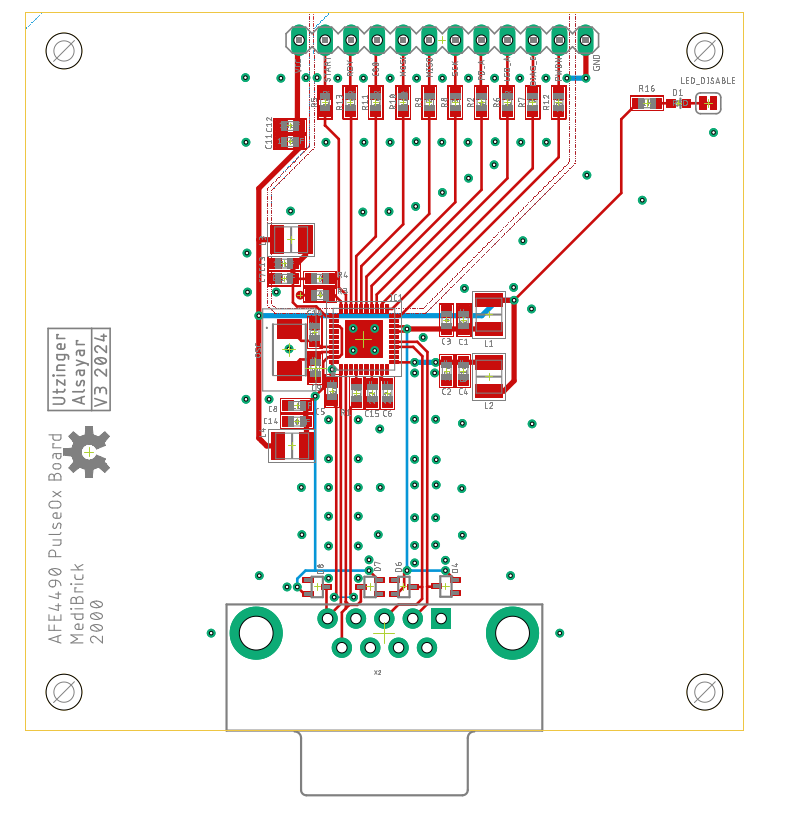
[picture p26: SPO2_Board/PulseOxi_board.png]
  
</a>

The following files are needed for PCB manufacturing and assembly.

- [Bill of Materials](PulseOxi_BOM.xlsx)
- [Manufacturing Files](PulseOxi_2024-05-09.zip)
- [Pick and Place](PulseOxi_PnP.xlsx)

The Bill of Materials is formatted so that its compatible with PCBWay submissions.

## 3D Printed Parts &#9881;
These are the links to the OnShape Design files, which you can edit and modify if you have an OnShape account (OnShape has free academic accounts).

- Medi Brick
  - [Brick Top](https://cad.onshape.com/documents/be6b7e5f847d89f3ec5eb9d5/w/761fee9865ca7ef709028476/e/ff897b4f359cec83b782ff14)
  - [Brick Bottom](https://cad.onshape.com/documents/92ad78475e8f0b17ff5e260b/w/88a02abbcb12cdbd4d9de3ad/e/fb79ca58ad2b6a0298e9d1b6)
  - [Brick Assembly](https://cad.onshape.com/documents/11cbfe9c3c739b6e8ecbf3d7/w/989b564ecd7f6d069e643ac0/e/85542f706be8cc7554218e8d)
  - [PulseOxi Brick Side Plate](https://cad.onshape.com/documents/bcb286d5b9de6189ba796e00/w/0a567208a5b563fc8cacc531/e/c605a2f5695bfb70bc8e7631)

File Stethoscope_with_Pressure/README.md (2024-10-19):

# Stethoscope with Pressure Sensor

<a href="..\assets\pictures\Stethoscope_Front_Closed_with_Plugins.jpg" target="_blank" style="float: right; margin-left: 20px;">
  
</a>

This stethoscope pressure solution consists of a sound as well as pressure recorder. For sound the I2S (Inter-Integrated Circuit Sound) bus is used to communicate with the microcontroller. This interface allows streaming and recording audio to an audio codec board. The Everest Semiconductor [ES8388 audio codec](datasheets\ES8388.pdf) was chosen because its supported by Arduino Audio Tools and Arduino Audio Driver and because Espressif created the Lyrat Audio modules with published reference [designs](datasheets\esp32-lyrat-v4-schematic.pdf). Sound is recorded with pui audio analog MEMS microphones [AMM-2742](datasheets\Microphone-AMM-2742-T-R.pdf) that are mounted on the printed circuit board. Two microphones are used where one is connected to the stethoscope and the other recording the background. An [dual differential amplifier](datasheets\opa344.pdf) is used to low pass filter and amplify the signal from the microphone, however amplification would not be needed for the ES8388 codec. Pressure is measured with a Honeywell MPR pressure sensor [MPRLS0300YG](datasheets/MPR_Pressure_HWSC_S_A0016036563_1-3073392.pdf) that convers the physiological range of 0 to 200 mm Hg.  

## Costs &#36;

| Item        | Quantity at Purchase | Costs  | Source            | Cost per Brick
|---                          | ---  | ---    | ---               | ---
| Microcontroller             |  1   | $17.5  | [Adafruit](https://www.adafruit.com/product/5477)          | $17.5
| Display                     |  5   | $13    | [Amazon](https://a.co/d/1QH0Ab9)            | $3
| Button                      | 25   | $9     | [Amazon](https://a.co/d/8KAuTwC) | $0.5 
| Battery                     |  1   | $10     | [Adafruit](https://www.adafruit.com/product/258)        | $10
| PCB                         |  5   | $45.18 | PCBWay            | $9
| Parts and Assembly          |  2   | $56.55 | PCBWay            | $29
| MPRLS0300YG (pressure)      |  2   | $35    | Sager Electronics | $17.5
| Stethoscope                 |  1   | $25    | [Amazon](https://a.co/d/7tQgoKs) | $25
| Arm Cuff                    |  1   | $17    | [Amazon](https://a.co/d/gKueGYV) | $17
| Assorted Wires              |8m    | $15    | [Amazon](https://a.co/d/58djefc) | $1
| Assorted Screws and Nuts    |100   |  $7    | Amazon            | $0.05
| Silocone Tubing             |  1   |  $9    | [Amazon](https://a.co/d/5GLJtFr) | $2
| Luer Lock female 3/32 barb  | 10   |  $9    | [Amazon](https://a.co/d/hxruOyw) | $1
| Luer Lock male 5/32 barb    | 10   |  $8    | [Amazon](https://a.co/d/c4cmtBQ) | $1
| Stainless Steel Tubing      |250mm | $10    | Amazon            | $2
| Assorted 3D printed parts   |      |        |                   | $3
|                             |      |        |                   |
| **Total with blood pressure**     |      |        |                   | **$140**
| **Total without blood pressure**  |      |        |                   | **$100**

Electronic components excluding the pressure sensor are $14 per board.

The pressure sensor was mounted in house as the PCB assembly service did not have access to inexpensive source.

## Test Software &#128187;
Test software is located in the Arduino folder.

| Folder | Description | 
|--- |---|
|MediBrick_Stethoscope_ES8388_to_CSV | Prints the two channel audio signal to the serial port for visualization with SerialUI application|
| MediBrick_Stethoscope_ES8388_TestSound | Creates test tone in left and right channel for head phones
| MediBrick_Stethoscope_ES8388_to_Headphone | Plays the recorded sound to the headphone
| MediBrick_Stethoscope_PressureTest| Test the arm cuff pressure sensor

## Microcontroller Software : &#9000;
Not available yet.

## Electronics Design &#128268;

<a href="Sound_schematic.pdf" target="_blank">
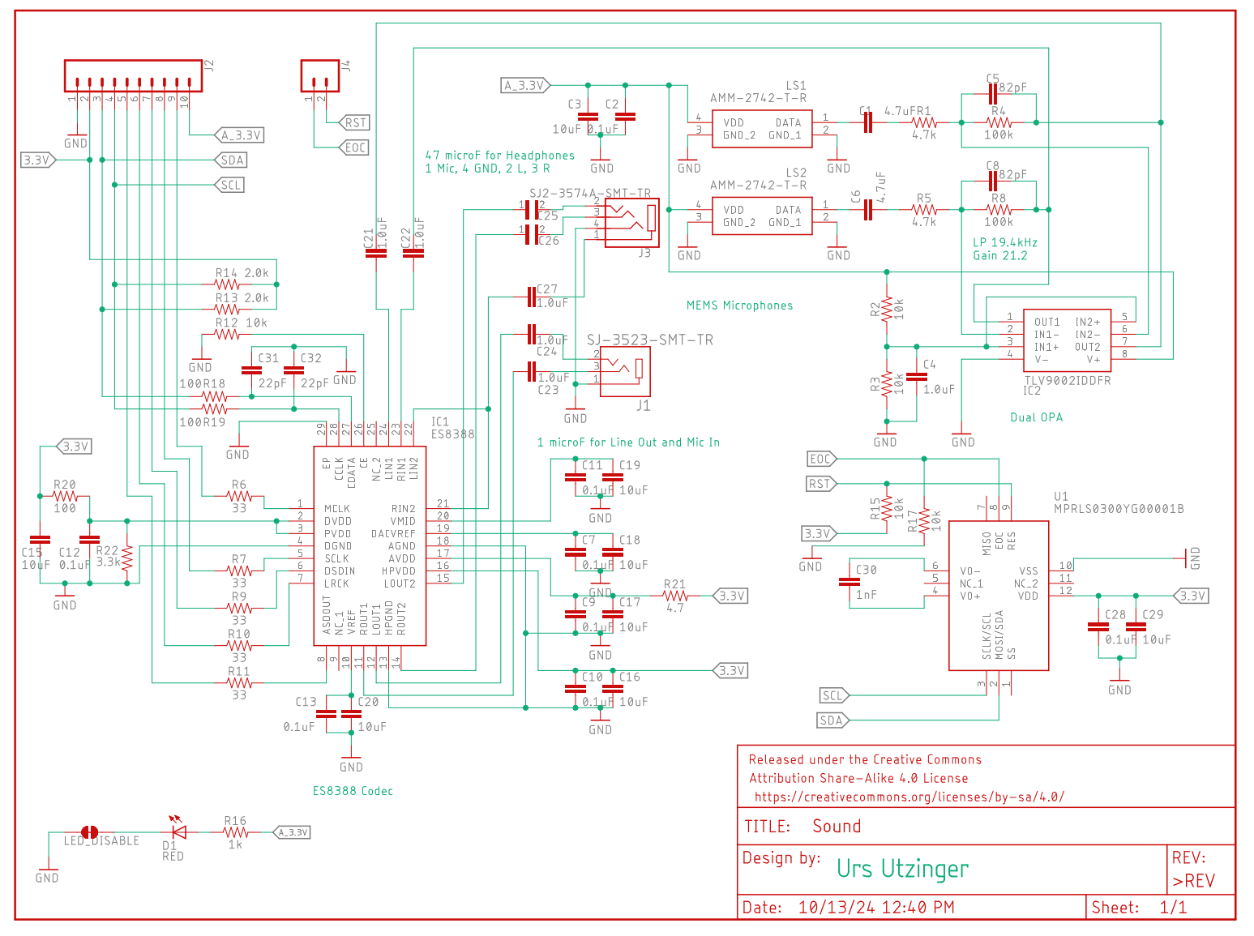
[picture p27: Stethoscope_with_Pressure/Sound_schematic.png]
  
</a>
<a href="Sound_board.pdf" target="_blank">
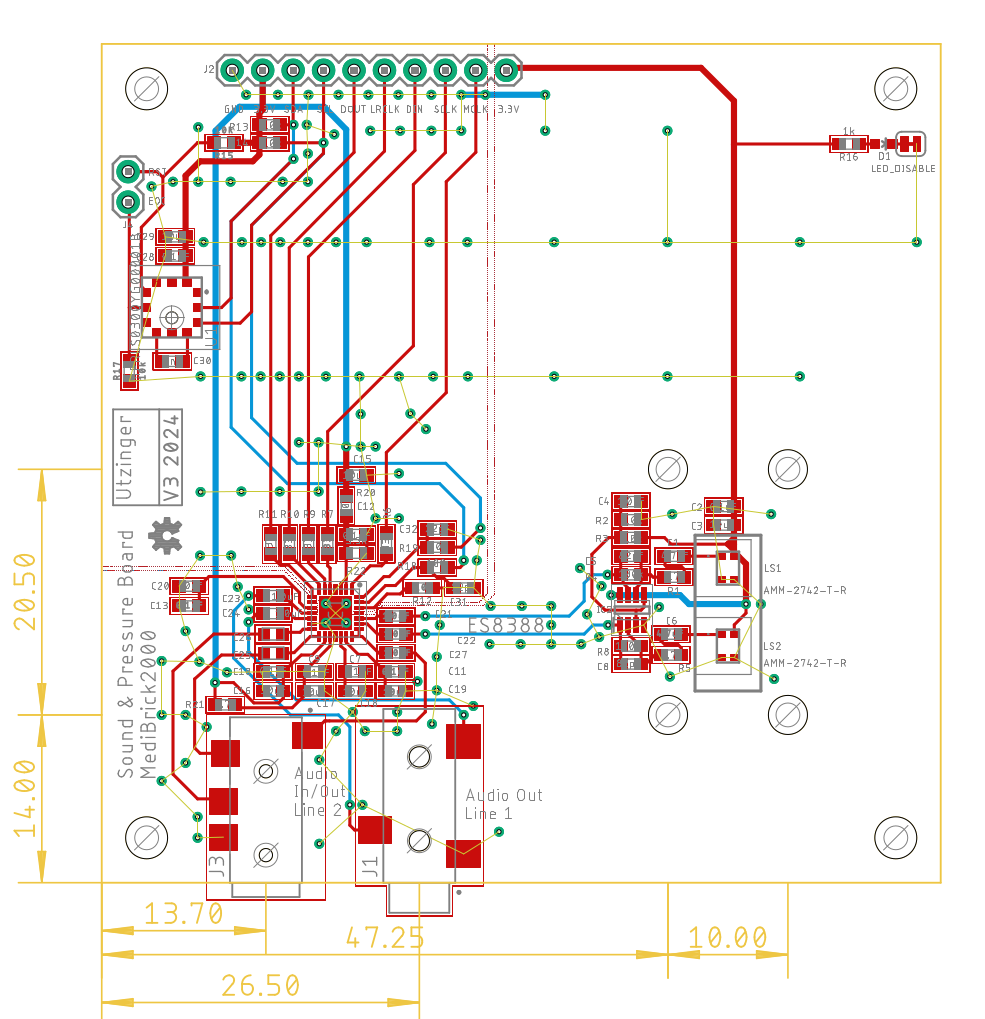
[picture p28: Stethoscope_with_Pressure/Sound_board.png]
  
</a>

The following files are needed for PCB manufacturing and assembly.

- [Bill of Materials](Sound_BOM.xlsx)
- [Manufacturing Files](Sound_2024-10-16.zip)
- [Pick and Place](Sound_PnP.xlsx)

The Bill of Materials is formatted so that its compatible with PCBWay submissions.

## 3D Printed Parts &#9881;
These are the links to the OnShape Design files, which you can edit and modify if you have an OnShape account (OnShape has free academic accounts).

- Microphone Housing
  - [Stethoscope Microphone Bottom](https://cad.onshape.com/documents/f23280f0a46d3d6c755669df/w/b75e085438cd92ba1b26b647/e/00c40c7437b1518e003bac9d)
  - [Stethoscope Microphone Top](https://cad.onshape.com/documents/ef2b037c38f1baa1c0b23c04/w/556b341c46d5852ab7c96559/e/758f32969c2d9c1e8976b746)
  - [Stethsocope Microphone Assembly](https://cad.onshape.com/documents/d283f9d6f3aaa55053af4362/w/49cecc8fd4c274541d804894/e/971484d9434ce01aa62acc7a)

  <a href="Models\Assembly.jpg" target="_blank">
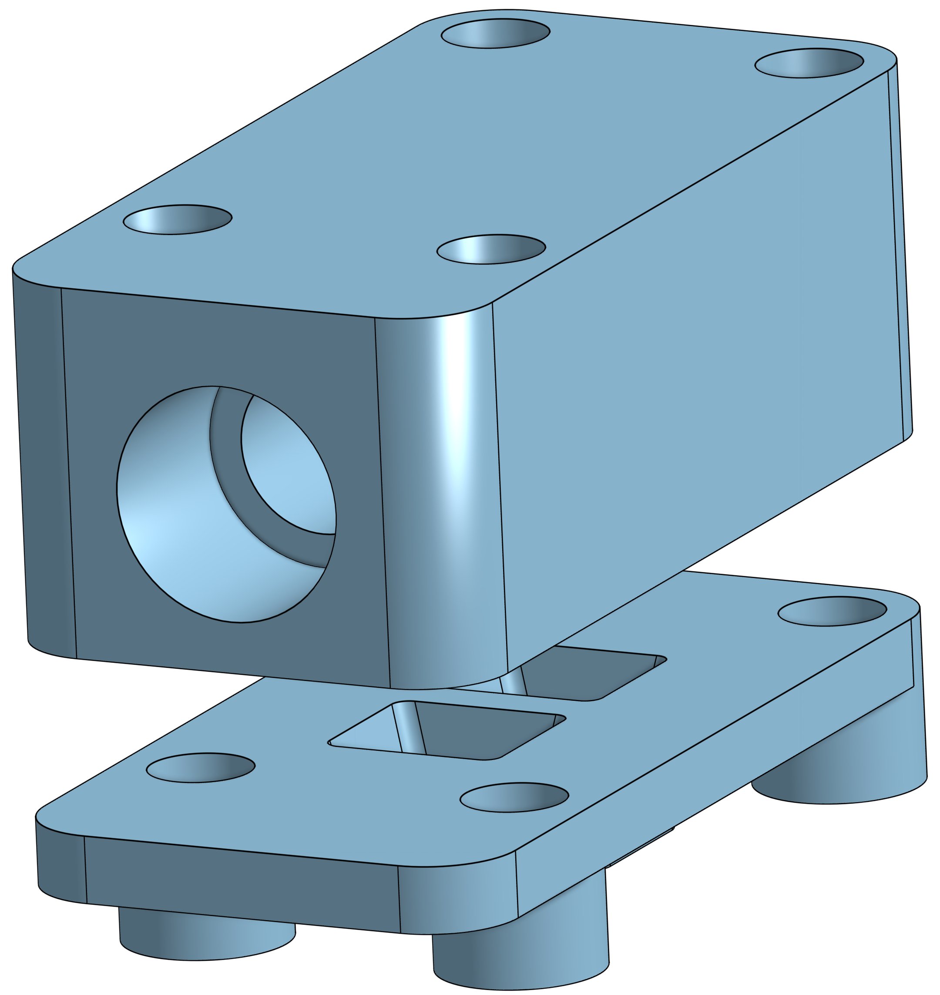
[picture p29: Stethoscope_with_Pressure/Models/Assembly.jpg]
    
  </a>

- Medi Brick
  - [Brick Top](https://cad.onshape.com/documents/be6b7e5f847d89f3ec5eb9d5/w/761fee9865ca7ef709028476/e/ff897b4f359cec83b782ff14)
  - [Brick Bottom](https://cad.onshape.com/documents/92ad78475e8f0b17ff5e260b/w/88a02abbcb12cdbd4d9de3ad/e/fb79ca58ad2b6a0298e9d1b6)
  - [Brick Assembly](https://cad.onshape.com/documents/11cbfe9c3c739b6e8ecbf3d7/w/989b564ecd7f6d069e643ac0/e/85542f706be8cc7554218e8d)
  - [Stethoscope Plate ](https://cad.onshape.com/documents/06546d5c2b6ecb0931149c5d/w/2aa54258cb58c3e795c7fea9/e/823e2851771a01788a8faacf)

## Filter Design Software

The software uses a digital high and low pass filter with cut on at 35Hz and cut off at 2kHz to improve sound quality. The coefficients are computed with a [python program](Compute_Filter_Coefficients.py).

The frequency content of the stethoscope audio was referenced with papers listed in the code's comment. 

<a href="filter_responses.svg" target="_blank">
  
</a>

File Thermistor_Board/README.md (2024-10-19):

# Thermistor/Wheatstone Brick

<a href="../assets/pictures/Temp_Front_Closed_with_Plugins.jpg" target="_blank" >
  
</a>

This Thermistor solution is based on a calibrated Wheatstone bridge. The Voltage potential over the thermistor is measured  and compared to a fixed voltage divider. Three thermistors can be measured using the micro controllers internal analog to digital converter. In order to achieve accuracy, the ADC is run a audio frequencies and measurements are averaged. Although ESP32 internal ADC is not of high quality, with the help of linearization and signal averaging, accurate temperature readings are achieved. 

## Costs &#36;

| Item        | Quantity at Purchase | Costs  | Source            | Cost per Brick
|---                          | ---  | ---    | ---               | ---
| Microcontroller             |  1   | $17.5  | [Adafruit](https://www.adafruit.com/product/5477)          | $17.5
| Display                     |  5   | $13    | [Amazon](https://a.co/d/1QH0Ab9)            | $3
| Button                      | 25   | $9     | [Amazon](https://a.co/d/8KAuTwC) | $0.5 
| Battery                     |  1   | $10     | [Adafruit](https://www.adafruit.com/product/258)        | $10
| PCB                         |  5   | $45.20  | PCBWay            | $9
| Parts and Assembly          |  2   | $99.16* | PCBWay            | $50
| Thermistors MA1000GG103AN **|  1   | $6      | [Amphenol](https://www.mouser.com/ProductDetail/Amphenol-Advanced-Sensors/MA100BF103AN?qs=wrT8kFYR7791l5TjYdzP%252BA%3D%3D) | $6
| 3.5mm male audio connector  | 10   | $10    | [Amazon](https://a.co/d/bbEIi9s) | $1
| Assorted Wires              |8m    | $15    | [Amazon](https://a.co/d/58djefc) | $1
| Assorted Screws and Nuts    |100   |  $7    | Amazon            | $0.05
| Assorted 3D printed parts   |      |        |  | $3
|                             |      |        |                   |
| **Total**                   |      |        |                   | **$100**

*Electronic components are $12 per board. 

**MA100BF103 also comes in less accurate and less expensive versions: MA100BF103BN and  MA100BF103CN.

## Test Software &#128187;
Test software is located in the Arduino folder.

| Folder | Description | 
|--- |---|
|MediBrick_Temperature_Test | Computes calibrated temperature. |

## Microcontroller Software : &#9000;
Not finalized yet

## Electronics Design &#128268;

<a href="Temp_schematic.pdf" target="_blank">
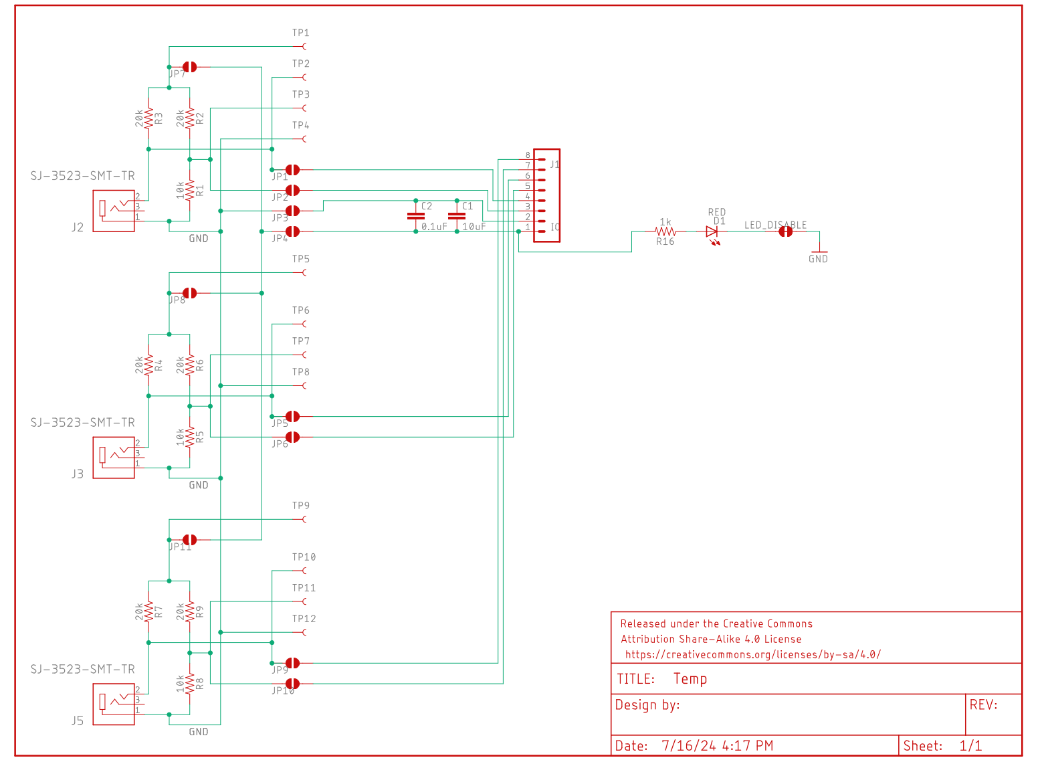
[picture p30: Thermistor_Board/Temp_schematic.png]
  
</a>
<a href="Temp_board.pdf" target="_blank">
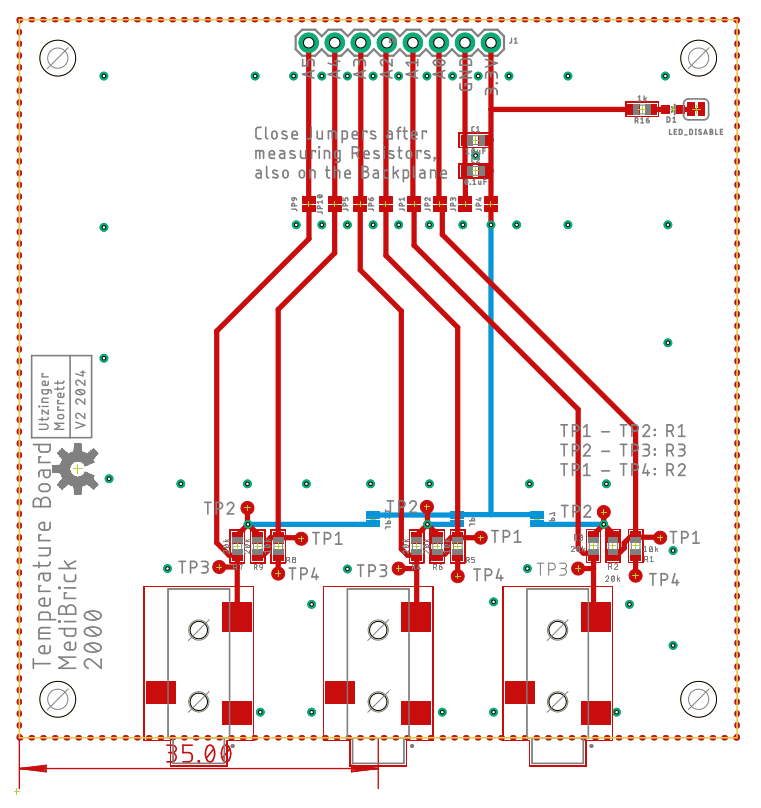
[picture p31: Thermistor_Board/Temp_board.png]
  
</a>

The following files are needed for PCB manufacturing and assembly.

- [Bill of Materials](Temp_BOM.xlsx)
- [Manufacturing Files](Temp_2024-07-16.zip)
- [Pick and Place](Temp_PnP.xlsx)

The Bill of Materials is formatted so that its compatible with PCBWay submissions.

## 3D Printed Parts &#9881;
These are the links to the OnShape Design files, which you can edit and modify if you have an OnShape account (OnShape has free academic accounts).

- Medi Brick
  - [Brick Top](https://cad.onshape.com/documents/be6b7e5f847d89f3ec5eb9d5/w/761fee9865ca7ef709028476/e/ff897b4f359cec83b782ff14)
  - [Brick Bottom](https://cad.onshape.com/documents/92ad78475e8f0b17ff5e260b/w/88a02abbcb12cdbd4d9de3ad/e/fb79ca58ad2b6a0298e9d1b6)
  - [Brick Assembly](https://cad.onshape.com/documents/11cbfe9c3c739b6e8ecbf3d7/w/989b564ecd7f6d069e643ac0/e/85542f706be8cc7554218e8d)
  - [Temperature Brick Side Plate](https://cad.onshape.com/documents/dac7e67c5b0270015712d245/w/d60526c34fb0e9aab2c02a4b/e/a363f2f519f137cd253c6eda?renderMode=0&uiState=6712d9ca15dc976491f436f6)

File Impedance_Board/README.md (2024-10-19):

# Tissue Impedance

IEC 60601 limits 100 µA maximum dc-leakage current through the body under normal conditions and 500 µA maximum under worst-case, single-fault conditions. An impedance circuit should not exceed that current.

## Analog Front Ends
### Analog Devices
- [AD5933 12-bit impedance converter ($18)](https://www.analog.com/en/products/ad5933.html) evaluation kit available ($68)
- [User Guide with reference schematics](https://www.analog.com/media/en/technical-documentation/user-guides/UG-364.pdf)

### Maxim AFE
- Biopotential
  - ECG (waveform)
  - R-R (heart rate)
- Bioimpedance
  - Resp (respiration)
  - GSR (galvanic skin response, stress level)
  - EDA (electro dermal activity)

- [Max 30001G ($10)](https://www.maximintegrated.com/en/products/analog/data-converters/analog-front-end-ics/MAX30001G.html) for Biopotential and Bioimpedance, evaluation kit available ($113)
- [Maxim 30009](https://www.maximintegrated.com/en/products/sensors/MAX30009.html) for Bioimpedance, evaluation kit available ($212)

### Summary of AFEs
| PART | Features             | Resolution | Remarks |
|---   |---                   |---         |---      |
| AD5933    | Single channel 3 wire | 12bit, 1Msps, 100kHz excitation| First Gen, 1024 point FFT, 1kOhm - 1MOhm
| AD5940/41 | 2 channel, 4 wire | 16bit, 800ksps, 200kHz | Impedance spectroscopy
| ADuC355   | 2 channel, 4 wire | 16bit, 800ksps, 200kHz | Impedance Spectroscopy, 26MHz ARM Cortex M3 MCU
| MAX30002  | single channel, BioZ, 2 or 4 wire | 17bit| 
| MAX30009  | single channel, BioZ, 2 or 4 wire | 16 kHz - 806 kHz |
| MAX30131/132/134 | 1-,2-,4- channel | 12 bit |
| MAX30001G | single channel, 2 or 4 wire | | Impedance and Potential (ECG)

## AD5933 for Bioimpedance

The AD5933 is a network analyzer IC that together with external circuitry can be used for bioimpedance measurements.

 

From [1] and [2], made with https://www.circuit-diagram.org/editor

### AD5933 Evaluation Board

The evaluation board from Analog Devices includes the reference design describing an analog front end to measure low impedances.

On the excitation side it has a passive high pass filter with $R_{HP}$, $C_{HP}$ and an OpAmp buffer.

On the measurement side it has an amplifier with $V_{DD}/2$ on the positive input and feedback resistor RFB.

The input to the AD5933 has $R_{AD_{IN}}$ of 20K as well as a $R_{AD_{FB}}$ of 20K.

### USING AD5933 for Bioimpedance Measurements

Munoz et al [2] describe their implementation in a 2022 paper. Several other web publications exist using that design.

For bioimpedance measurements the following analog front end elements should be used: a high-pass filter (HPF), a voltage-to-current converter (VCC), and an instrumentation amplifier (INA).

The HPF is a first order system composed of a 100 kΩ resistor and a 10 nF capacitor to remove the DC components of $V_{out}$. $f_c = 1 / (2 \pi R C)$ resulting in 160Hz. 

The HPF output is connected to VCC, which consists of an operational amplifier and two resistors. The current injected into the tissue should not exceed 10 uA. 

$R_{VCC current} = 1 kΩ$ (This will exceed 10 µA!)

$R_{VCC_{protect}} = 10 kΩ$

Because the impedance is supposed to vary from tens to hundreds of ohms, 

$R_{feedback} = 10 kΩ$ 

ensures that current flows mainly through $Z_{Load}$, which is connected in parallel to $R_{feedback}$.

The current through VCC is

$R_{VCC_{curent}} = (V_{out} - V_{ref}) / R_{VCC_{current}}$. 

Therefore the voltage over $Z_{load}$ is

$V_{Z_{load}} = -(V_{out} - V_{ref}) / R_{VCC_{current}} * Z_{load}$.

The unity gain instrumentation amplifier receives, through its non-inverting input, the voltages on the electrodes connected to $Z_{load}$. Since the ADC converter of the AD5933 is unipolar, a potential ($V_{ref}$) is added as reference voltage to the instrumentation amplifier. The output of the INA is 

$V_{INA} =  V_{load} + V_{ref}

The current through $R_{AD_{IN}}$ is:

$(V_{INA} - V_{ref})/R_{AD_{IN}}$

The output of the internal OpAmp in the AD5933 is 

$I_{RFB} * R_{AD_{FB}}$

Therefore 

$V_{AD5933} = (V_{INA} - V_{ref})/R_{AD{IN}} * R_{AD_{FB}}$.

The DSP of the AD5933 calculates the real and imaginary parts of $Z_{load}$, which are read through an inter-integrated circuit (I2C) protocol by a micro controller.

### External Electrical Components for AD5933

A list of designs using the AD5933 used the following values for resistors and capacitors:

| Design        | $C_{HP}$ | $R_{HP}$ | $RFB$ | $R_{VCC_{current}}$ | $R_{VCC_{protect}}$ | $R_{INA_{GAIN}}$ | $R_{REFGEN}$ | $R_{AD_{IN}}$ | $R_{AD_{FB}}$ | $VCC +$
|---            |---   |---    |---   |---            |---              |---            |---       |---      |---      |---
| Eval [1]      | 47nF | 49.9k | 200k | N.A.          | N.A.            | N.A.          | 49.9k    | 20k     | 20k     |
| Datasheet [3] | 47nF | N.S.  | N.S. | N.A.          | N.A.            | N.A.          | N.S.     | 20k     | 20k     |
| Munoz [2]     | 10nF | 100k  | N.A. | 1k            | 10k             | Gain=1        | 1k       | 1k      | 1k      | GND
| Instru Bio [4]| 10nF |  10k  | N.A. | 1k            |  1k             | Gain=10,5.5k  | VDD/2    | 1k      | 1k      | GND
| Instru BIA [5]| 10nF | 100k  | N.A. | 1M            |  1M             | Gain=1.5,100k | VDD/2    | 1k      | 1k      | GND
| Instru BIA [6]| 10nF | 100k  | N.A. | 285k          |  1M             |               | VDD/2    |         |         | VDD/2
| Instru Thor[7]| 1.2nF|  10k  | N.A. | 1M            |  1M             | Gain=1.5,100k | 1k       | 1k      | 1k      | GND
| Instru Thor[8]| 100nF|  20k  | N.A. | 100k          |  10k            | Gain=1.5,100k | 3.2/1k   | 1k      | 1k      | GND
| UA 2023       | 10nF | 100k  | N.A. |  82k          |  82k            | Gain=51,1k    | 20k      | 20k     | 20k     | VDD/2
| UA 2024       | 10nF | 100k  | 200k | 265k          |   1k            | Gain=51,1k    | 10k      | 20k     | 20k     | VDD/2

Common active components used for AD5933 biomimpedance:
- Network Analyzer AD5933
- Operation Amplifier(s) AD8608 or AD8606 or AD8605
- Instrumentation Amplifier INA826AID

#### High Pass
- $1 / (2 \pi R C)$, should attenuate 50 and 60Hz, need 200Hz..xxkHz
- 10nF, 100k fc=160Hz

#### $R_{current}$ and $R_{protect}$
- Input into VCC is at 1.65V offset with 1V amplitude. With $I_{CC} <10uA$ and $V_{CC} = 2.65V$ and $R_{VCC_{current}}$ will need to be 265kΩ.
- Setting of Range 1 in AD5933 is 1V if operating at 3.3V., for $10 \mu A$ we need 110kΩ for $R_{VCC_{current}}$.
- Analog Devices: "Bio-Impedance Circuit Design for Body Worn Systems"

#### $R_{Gain}$ 
- $G = 1 + (49.4k/R_{Gain})$
- With $R_{INA_{GAIN}}$  = 1kΩ the gain will be $G=51$

### Impedance Estimation

Formula to compute impedance from measurements: Description to be completed (check evaluation board and Instructables, also search PubMed).

### References

For general reading: [Analog Devices: Bio-Impedance Circuit Design for Body Worn Systems"](https://www.analog.com/en/resources/analog-dialogue/articles/bioimpedance-circuit-design-challenges.html)

1) [Analog Devices AD5933 Evaluation Board, User Guide](https://www.analog.com/media/en/technical-documentation/user-guides/UG-364.pdf)
2) [Munoz et al](https://doi.org/10.1016%2Fj.ohx.2022.e00274)
3) [AD5933 Datasheet](https://www.analog.com/media/en/technical-documentation/data-sheets/AD5933.pdf)
4) [Instructables Body Composition](https://www.instructables.com/Determining-Body-Composition-using-Arduino)
5) [Instructables BIA 1](https://www.instructables.com/Body-Composition-using-BIA/)
6) [Instructables BIA 2](https://www.instructables.com/Bio-Impedance-Analysis-BIA-With-the-AD5933/)
7) [Instructables Thor 1](https://www.instructables.com/Thoracic-Impedance-1/)
8) [Instructables THor 2](https://www.instructables.com/Thoracic-Impedance/)
9) [IEEE Tutorial](https://ieeexplore.ieee.org/document/9529213)
10) [Uwe Pliquett, Andreas Barthel, 2012 J. Phys.: Conf. Ser. 407 012019](https://iopscience.iop.org/article/10.1088/1742-6596/407/1/012019)
10) [Paco Bogonez-Franco et al, 2014, Problems encountered during inappropriate use of commercial bioimpedance devices in novel applications, 7 th International Workshop on Impedance Spectroscopy 2014](https://www.researchgate.net/publication/269571754_Problems_encountered_during_inappropriate_use_of_commercial_bioimpedance_devices_in_novel_applications)
12) [J Ferreira et al 2010 J. Phys.: Conf. Ser. 224 012011](https://iopscience.iop.org/article/10.1088/1742-6596/224/1/012011/pdf)

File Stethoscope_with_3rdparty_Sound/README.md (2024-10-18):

# Sound Solution with 3rd Party ES8388 Audio Breakout Board

The Sound Sensor module records the sounds of heartbeats and the lungs. The sensor (electret microphone) is connected to a stethoscope tube, so the user can mimic the functionalities of an "analog" stethoscope. 

This solution is likely not functional because the PCB Artist Board does not implement a low pass filter on the I2C data lines. Once I2S is started and transferring data the noise on the I2C is too large to function properly and other boards solve this issue with a low pass filter on I2C data and clock lines.

## Schematic

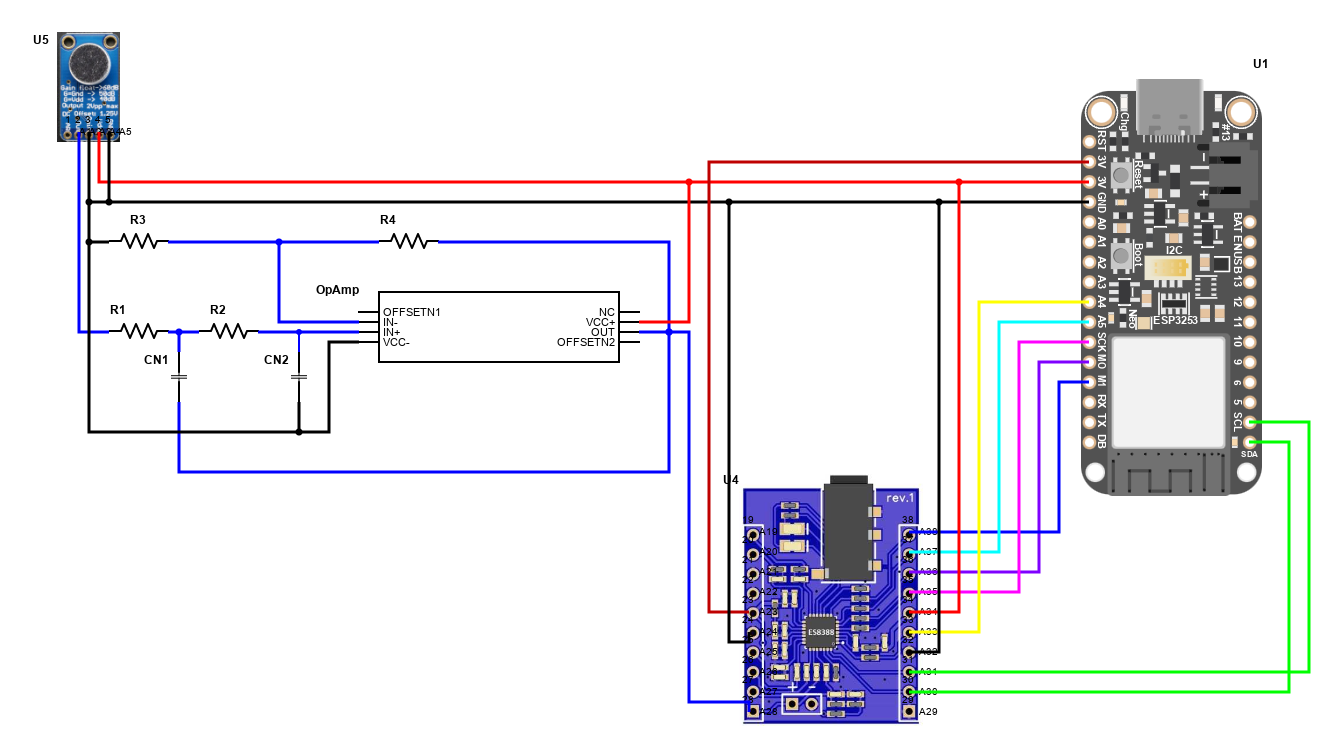
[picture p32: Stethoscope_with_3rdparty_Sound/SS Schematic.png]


## Elcret Microphone
Enter Amazon source here

## [ES8388 PCB Artist Audio Board](https://pcbartists.com/es8388/)

Here we describe the connection between the PCB Artist baord with the EPS32 S3 and the corresponding settings in the AudioTools library.

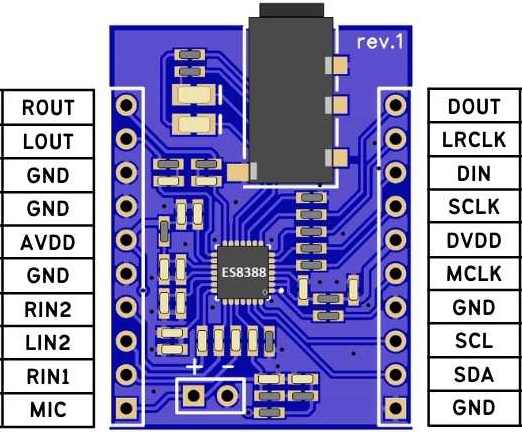
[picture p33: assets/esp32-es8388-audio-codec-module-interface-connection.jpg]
ES8388


| Name | ESP32 S3 | ES8388   | ES8388 | ESP32 S3 | Name        | Frequency (max)
|---   |---       |---       |---     |---       |---          |  ---
| RO   | NC       | ROUT     | DOU    | 37/MI    | D OUT       |
| LO   | NC       | LOUT     | LRCLK  | A5/8     | WS/Word CLK | 200 kHz
| GND  | NC       | GND      | DIN    | 35/MO    | D IN        |
| GND  | GND      | GND      | SCLK   | 36/SC    | Bit CLK     | 26MHz
| 3.3  | 3.3 V    | AVDD     | DVDD   | 3.3 V    | 3.3 V       |
| GND  | NC       | GND      | MCLK   | A4/14    | Master CLK  | 51.2MHz
| RI   | NC       | RIN2     | GND    | NC       | GND         |
| LI   | NC       | LIN2     | SCL    | 4        | SCL         | 400Khz
| RI   | NC       | RIN1     | SDA    | 3        | SDA         |
| MIC  | NC       | LIN1/MIC | GND    | NC       | GND         |

$MIC_1$ is connected to MIC.
$MIC_2$ is connected to RI.
R/LO are routed.
R/LI are routed.

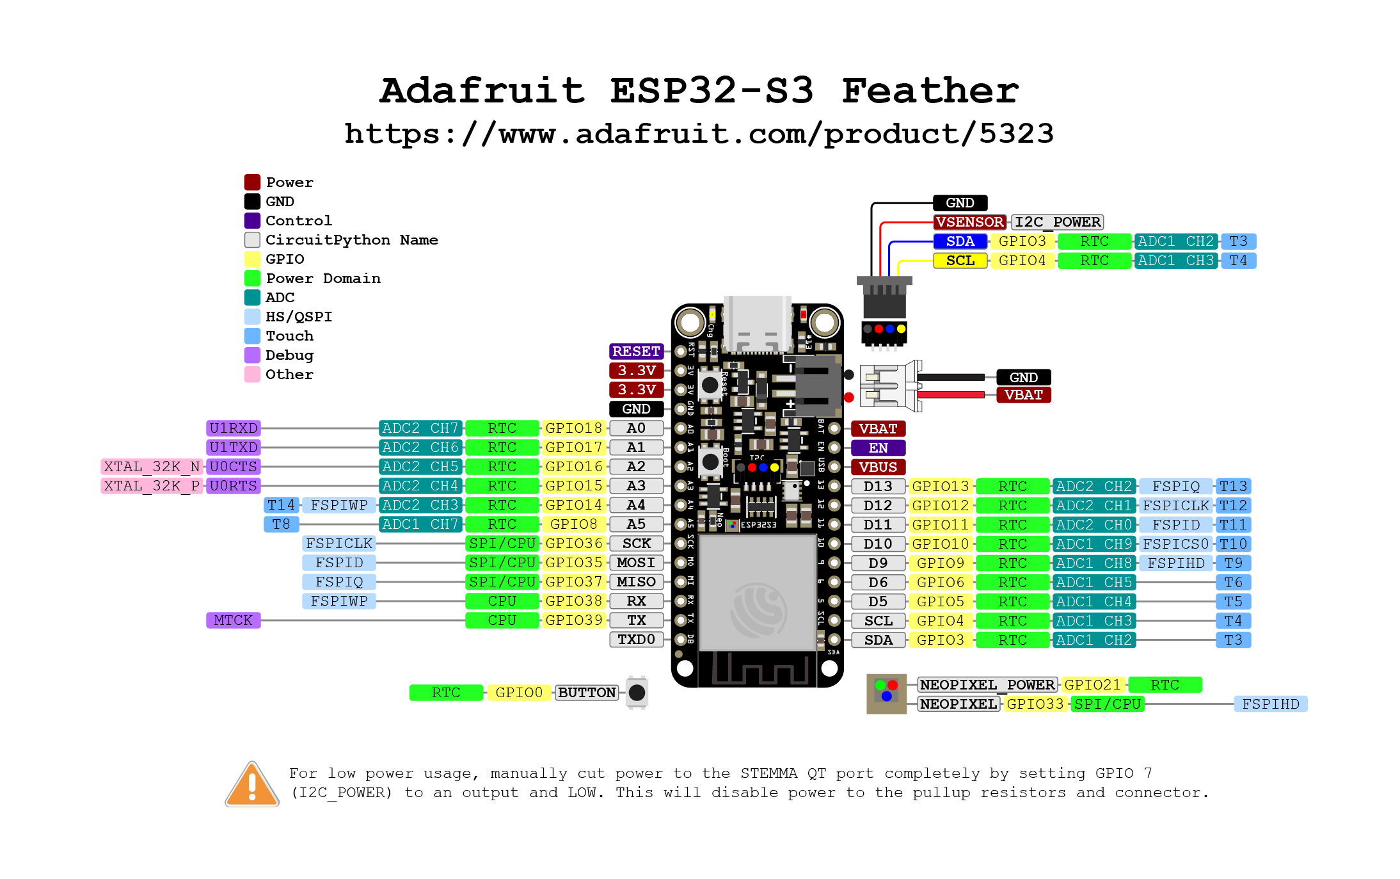
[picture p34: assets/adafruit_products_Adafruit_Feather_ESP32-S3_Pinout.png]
Adafruit Feather ESP32 S3


### Audio Driver Setup

```
#include "AudioTools.h"
#include "AudioLibs/I2SCodecStream.h"

// I2C
#define SDAPIN               3
#define SCLPIN               4
#define I2CSPEED        100000
#define ES8388ADDR        0x10

// I2S
#define MCLKPIN             14
#define BCLKPIN             36
#define WSPIN                8
#define DOPIN               37
#define DIPIN               35

AudioInfo                     audio_info(44200, 2, 16);
SineWaveGenerator<int16_t>    sine_wave(32000);
GeneratedSoundStream<int16_t> sound_stream(sine_wave);
DriverPins                    my_pins;
AudioBoard                    audio_board(AudioDriverES8388, my_pins);
I2SCodecStream                i2s_out_stream(audio_board);
StreamCopy                    copier(i2s_out_stream, sound_stream);
TwoWire                       myWire = TwoWire(0);

void setup() {

  Serial.begin(115200);
  AudioLogger::instance().begin(Serial, AudioLogger::Warning);
  LOGLEVEL_AUDIODRIVER = AudioDriverWarning;
  delay(2000);

  Serial.println("Setup starting...");

  my_pins.addI2C(PinFunction::CODEC, SCLPIN, SDAPIN, ES8388ADDR, I2CSPEED, myWire);
  my_pins.addI2S(PinFunction::CODEC, MCLKPIN, BCLKPIN, WSPIN, DOPIN, DIPIN);

  my_pins.begin();
  audio_board.begin();
  auto i2s_config = i2s_out_stream.defaultConfig();
  i2s_config.copyFrom(audio_info);  
  i2s_out_stream.begin(i2s_config);
  sine_wave.begin(audio_info, N_B4); // 493.88 Hz

  Serial.println("Setup completed ...");
}

// Arduino loop - copy sound to out
void loop() { copier.copy(); }
```

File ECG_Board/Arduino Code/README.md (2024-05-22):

The ECG sender code is based in Arduino (C++). This code can be used to run the Sparkfun AD8232 ECG Pre-amplifier code. This code also has a digital low-pass filter to remove some of the noise from the ECG reading. Lastly, each of the sensors has an OLED screen and a button. This code already takes this into account. 
The OLED can switch display between the ECG reading and the battery percentage and discharge rate. Readings from the ECG is in millivolts. For the battery percentage and discharge rate, a library from the battery management is added in the code.
The button is used to switch said OLED display. This button can also be used to put the ESP32 into deep sleep. Pressing the button for one second switches the display, and holding it for 5 seconds puts the ESP32 into deep sleep mode.

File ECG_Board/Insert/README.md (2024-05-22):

This is the insert for the ECG Sensor Casing

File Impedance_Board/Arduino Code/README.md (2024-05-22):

This is a description for the Arduino Code

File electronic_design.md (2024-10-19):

# Electronic Design

All electronic designs were completed with EagleCAD. The files can also be imported into KiCAD as EagleCAD will no longer be supported by its owner.

Files ready for submission to PCB manufacturer (PCBWay) are in each project subfolder.

## Eagle CAD settings
The design used the following settings:

### Grid
-Size: 1mm
-Alt: 0.1mm

### DRC (Design Review ...)

Units are mil, second value given below is for Waver Level Packaging (very small ICs)

- Layers: Core 1.5mm
- Clearance: Different Signals: Wire-Wire:6, Wire-Pad:6/3. Wire-Via:6/3, Pad-Pad:6, Pad-Via:6/3, Via-Via:6/3
- Clearance: Same Signals: Smd-Smd:6/3, Pad-Smd:6/3,Via-Smd:6/0
- Distance: Copper/Dimension:40, Drill-Hole:6
- Sizes: Min:6/4, Drill:0.35/0.1mm, MicroVia:9.99/0.1mm, BlineViaRatio:0.5/0.05
- Annular Ring: Pads Top:10/3,25%,20 Inner:20/3.25%.20 Bottom:10/3,25%,20
- Annular Ring: Vias: Outer:8/2,25%,20 Inner:8/2,25%,20
- Annular Ring: MicroVias: Outer:4/3,25%,20 Inner:4/3,25%,20
- Shapes Smds Roundness 0,0%,0
- Shapes Pads Top: as in lib, Bottom: as in lib, First: not special, Elongation 100,100
- Supply: Termal isolation: 10
- Masks: Stop:4/3,100%,4 Cream:0,0,0 Limit 15
- Misc: Check font, check restrict, check names, check stubs, differential pairs 10mm, gap factor 2.5

## From CAD to Manufacturing

The BOM needs to matches the manufacturers requirement. 
Your design needs to match manufacturing tolerances. 
For micro vias or WLP you likely need to select advanced manufacturing settings at the manufacturers website.

1) Make sure your board has no errors (Tools->Errors)
2) Check on Manufacturing Tab the graphical representation of your manufactured board
3) CAM Processor -> Local CAM Jobs -> Each board has its own file.cam
    Enable ZIP (this creates Gerber file archive)
4) Upload.

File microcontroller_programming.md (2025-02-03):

# Software

Code included with this project is using the Arduino programming environment. 
Several comprehensive libraries as well as test programs for all sensors were developed for this project. 

## Data Visualization

- SerialUI: https://github.com/uutzinger/SerialUI
    - Python: https://www.python.org/downloads/
    - Python Packages: `pyqt5, pyqtgraph, pyopengl, numpy, pyserial, markdown`

SerialUI has similar functions as Arduino IDE serial monitor and serial plotter. However it has arguably better plotting and data visualization capabilities.

## Arduino Libraries
| Chip          | Manfacturer            |  Brick | Source | Example Program | Limitations
| ---           | ---                    | --- | --- | --- | --- |
| AFE44X        | Texas Instrumente      | Pulseoxi | [Utzinger](https://github.com/uutzinger/Arduino_AFE44XX) | Yes | No $SP_{O_2}$ yet |
| MAX30001G     | Maxim / Analog Devices | Bioimpedance and ECG | Utzinger | No | in progress |
| ES8336        | Everest                | Stethoscope | [Audio Driver Schatzman](https://github.com/pschatzmann/arduino-audio-driver) | Yes | tested |
| ES8336        | Everest                | Stethoscope | [Audio Tools, Schatzman](https://github.com/pschatzmann/arduino-audio-tools) | Yes | tested |
| MPRLS0300YG   | Honeywell              | Pressure |  [Sparkfun](https://github.com/sparkfun/SparkFun_MicroPressure_Arduino_Library) | No | to be worked on |
| ICM20948      | TDK                    | IMU | [Sparkfun](https://github.com/uutzinger/Arduino_ICM-20948) | Yes | need to decide on DMP or custom fusion (AHRS Madgwick) |
| BMP581        | Bosch                  | Pressure | [Sparkfun](https://github.com/uutzinger/Arduino_BMP581) | Yes | sometimes fails to start in SPI mode
| WS2812B       | World Semi             | Color LED strip | [Neopixel](https://github.com/uutzinger/Arduino_NeoPixel) | Yes | figure out individual pixel animation |
| SavitzkyGolay | Signal Proc            | Filter | [Utzinger](https://github.com/uutzinger/SavitzkyGolayFilter)| Yes | need to test with PulseOxi data |
| SHT45-AD1B    | Sensirion              | Humidity, Temperature | [Sensirion](https://github.com/uutzinger/Arduino_SHT) | Yes |  |
| SCD41D        | Sensirion              | CO2 | [Sensirion](https://github.com/uutzinger/Arduino_SCD4x) | Yes |  |  
| SGP41D        | Sensirion              | eVOC, eNOx | [Sensirion](https://github.com/uutzinger/Arduino_SGP41) | Yes | uses Gas Index |
| SEN5X         | Sensirion              | Particulate Matter | [Sensirion](https://github.com/uutzinger/Arduino_SEN5x) | Yes | |
| MICS 6814     | SGX Sensortech         | CO, NH3, NO2 | Utzinger | No | to be worked on (needs manual calibration and soldering)| 
| SSD1306       | Solomon Systems        | LCD display | [Adafruit](https://github.com/uutzinger/Arduino_SSD1306) | Yes |  |
| MAX1740X      | Maxim / Analog Devices | Battery monitor | [Sparkfun](https://github.com/uutzinger/Arduino_MAX1704x) | Yes | need to look into how to detect that the system is on battery |
| LC709203F     | ON Semiconductor       | Battery monitor | [Adafruit](https://github.com/uutzinger/Arduino_LC709203F) | No | not available in newer boards from Adafruit and Sparkfun|
| ESP ADC       | Espressif              | Temperature | [Audio Tools, Schatzman](https://github.com/uutzinger/arduino-audio-tools) | Yes | 6 channel recording with averaging and binning |
| Gas Index     | Sensirion              | Gas Index | [Sensirion Gas Index](https://github.com/Sensirion/arduino-gas-index-algorithm) | Yes | |
| Arduino Core  | Sensirion              | Arduino Core | [Sensirion Arduino Core](https://github.com/Sensirion/arduino-core) | Yes | |
| ESP DeeSleep  | Espressif | Deep Sleep | | Yes | |

## Integrated Development Environment

- [Arduino IDE](https://www.arduino.cc/en/software)
- [Arduino EPS32 Extension from Espressif](https://docs.espressif.com/projects/arduino-esp32/en/latest/installing.html)

Arduino ESP32 is comprehensive and supports the ESP32 internal peripherals as listed [here](https://docs.espressif.com/projects/arduino-esp32/en/latest/libraries.html)

### Arduino IDE Programmer Settings

When programming an ESP32 care must be taken on the proper memory and communication settings. During development the microcontroller will also need to be manually rebooted.

Sparkfun feather boards are more easily manageable as they have less options to configure in the IDE. Adafruit ESP32 boards come in a variety of memory configurations and since Adafruit promotes microPython their boot loader settings vary and are by default not set for the Arduino IDE.

Reboot of the ESP32 is accomplished in software by toggling serial control lines. However this is not reliable and sometimes powercycling is necessary.

If the microcontroller board can not be programmed a manual boot loader reset might be necessary (see below).

Programming support on Windows Platform appears to be more refined than on Linux platform.

Once the microcontroller is mounted inside the MediBrick and the battery is connected, manual reset and reboot are not longer accessible.

**Adafruit ESP32-S3 Feather with 2MB of PSRAM**

Reset to boot loader: 

- Push boot button and hold it. Push and release reset button. Release boot button.
- If this does not work, switch to a different USB port on your computer.

The default programming settings are not working well with Arduino IDE and each time the board is selected the following will need to bet chosen:

- USB CDC on Boot: "Enabled"
- CPU frequency: "240MHz (WiFi)"
- Code Debug Level: "None"
- USB DFU on boot: "Disabled"
- Erase all Flash: "Disabled"
- Events run on: "Core 1"
- Flash Mode: "QIO 80 MHz"
- Flash Size: "4Mb"
- Arduino runs on: "Core 1"
- Flash Size: "4Mb"
- USB Firmware MSC on Boot: "Disabled"
- Partition Scheme: "Default 4Mb with spiffs"
- PSRAM: "OPI-PSRAM"
- Upload mode: "UART0 / Hardware CDC"
- Upload speed" "91600"
- USB mode: "Hardware CDC and JTAG"
- Zigbee mode: "Disabled"

**Sparkfun ESP32 C WROOM**

Reset boot to loader: 

- With power cycle: Push and hold the boot button. Connect the board to a computer through the USB-C connection. Release the boot button.

- Without power cycle: Push and hold boot button. Press and release the RST button. Release the boot button. (not working on Linux)
- After programming is completed, reboot the MCU.
    - Press the RST button.
    - If that does not work Power cycle the board.

If you want to use QWIIC: GPIO 0 controls the power output from the XC6222 LDO regulator to the Qwiic connector. Users must toggle GPIO 0 high to enable power for the Qwiic

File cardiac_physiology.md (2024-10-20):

# Cardiac Physiology

## Circulatory System

<!-- Circulatory System Figure -->


<p style="text-align: center;">Figure: Circulatory System. Major genetically predetermined arteries and veins of the body.</p>

<!-- Flow Distribution Figure -->


<p style="text-align: center;">Figure: Flow distribution of the cardiac output.</p>

## Heart

<!-- Heart Anatomy Figure -->


<p style="text-align: center;">Figure: Heart Anatomy. Many of the signals measured in this project are defined by the activity of the left ventricle.</p>

<!-- Heart Contraction GIF -->
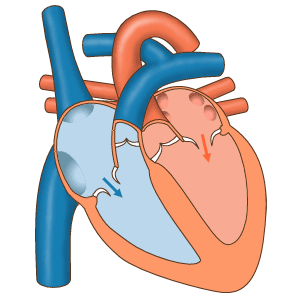
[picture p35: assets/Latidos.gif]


<p style="text-align: center;">Figure: Heart Contraction.</p>

## Wigger's Diagram

<!-- Wigger's Diagram Figure -->


<p style="text-align: center;">Figure: Wigger's diagram is an excellent tool to teach cardiac physiology, showing pressures found in the ventricle as well as the aorta and atrium. The sharp contraction resulting in the QRS complex and first heart sound as well as the second sound coinciding with the closure of the aortic valve. The repolarization of the heart muscle corresponding to the T wave.</p>

All figures https://commons.wikimedia.org/

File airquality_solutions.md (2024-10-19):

# Air Quality Solutions

## Particulate Matter

SEN5X family of sensors from Sensirion is a platform of compact particle sensors. They have a >10 years lifetime. Because they use a fan to create a steady stream of air in the sensor chamber, they create 24dB noise at a distance of 0.2m.  Common used parameters are PM1 (0.3-1 $\mu$ particles), PM2.5 (0.3-2.5 $\mu$), PM4(0.3-4 $\mu$), PM10 (0.3-10 $\mu$). They also measure Humidity and Temperature with an accuracy of $+/-4.5\%$ and $+- 0.45\degree C$.

There are the following models available:

- **SEN50 Particulate Matter** approx. $22.2
- SEN54 Particulate Matter, rel Humidity, Temperature, VOC Index, approx. $28.1
- SEN55 Particulate Matter, rel Humidity, Temperature, VOC Index, NOx Index, approx. $32.6

There are less expensive sensors available from [Winsen](https://shop.winsen-sensor.com/collections/particle-sensor)

## CO2

Sensirion makes accurate compact photo acoustic CO2 sensor. The sensor is negatively impacted by vibrations. Its not clear if the fan of a  particulate matter sensor impacts this sensor.

There are the following models available:

- **SCD40** 400-2000ppm, +/- 50ppm [datasheet](Airquality\datasheets\SCD4x_Ver1.4_Feb2023.pdf) approx. $29.7
- SCD41 400-5000ppm, high accuracy, low power [datasheet](Airquality\datasheets\SCD4x_Ver1.4_Feb2023.pdf) approx. $37.1
- SCD42 400-2000ppm, +/-75ppm [datasheet](Airquality\datasheets\CD_DS_SCD42_Datasheet_D1.pdf) no lonber available.

They also measure Humidity $+/-6/%$ and Temperature $+/-0.8 \degree C$ as the sensor signal is affected by those quantities.

There are less expensive sensors available from [Winsen](https://shop.winsen-sensor.com/collections/co2-sensor)

## Pressure

Bosch makes high quality pressure sensors with an altitude resolution in air of 25 cm.

- **BMP581**, 30 -125 kPa, ultra low noise of 0.1 Pa RMS, Temperature range of -40 to 85C [datasheet](Airquality\datasheets\bst_bmp581_ds004-2950309.pdf) approx. $4.12

## Humidity and Temperature

### Bosch

Bosch makes fully integrated airquality sensor that is commonly used for indor airquality assessment. But their CO2 is usually an electric estimate and the integrated circuits don't measure particulates.

- BME688 Pressure 0.6hPa, Humidity $+/-3\%$ Temperature $+/-0.5 \degree C$

### High Accuracy Temperature and Humidity Sensors

Many sensors need temperature compensation and some require humidity compensation. The Humidity and Temperature sensors that are integrated into other sensor are not of highest accuracy. higher quality sensors are available:

- SHT40, Humidity $+/- 1.8\%$, Temperature $+/-0.2 \degree C$, approx. $2.5
- SHT41, Humidity $+/- 1.8\%$, Temperature $+/-0.2 \degree C$, approx. $3.4
- SHT43, Humidity $+/- 1.8\%$, Temperature $+/-0.2 \degree C$, approx. $5.1
- **SHT45**, Humidity $+/- 1\%$,   Temperature $+/-0.1 \degree C$, approx. $6.4

## NOx & VOC

A variety of MEMS sensors can measure electrical equivalents of atmospheric gases through electro chemical reactions where the sensor element is heated and the presence of a gas reduces its resistance. Usually there is cross sensitivity within one element with other gases.

A typical Sensirion MEMS gas sensor consumes 3mA to measure VOC and NOX. It takes 10 seconds to detect a change in VOC and about 4 mins for NOx. Sampling is typically once per second.

- **SGP41 sensor**, VOC Index 1-500, NOX Index 1-500, $8.96 [datasheet](Airquality\datasheets\Sensirion_Gas_Sensors_Datasheet_SGP41.pdf)

## Carbon Monoxide, Amonia, Nitrogenoxide

Its difficult to find accurate and inexpensive Carbon Monoxide sensors. It is possible to calibrate less expensive sensors by measuring known levels of gases in a test chamber. For example, there should be no Carbon Monoxide in the atmosphere and a sensor signal outdoors indicates the sensor background level.

Carbon Monpoxide is a poisenos gas where as Nitric Oxide and Methane should be avoided indoors.

Amphenol produces an multi element MEMS gas sensor:

- **Amphenol SGX Sensortech, MiCS-6814 MEMS sensor** $13
[datasheet](Airquality\datasheets\1143_Datasheet-MiCS-6814-rev-8,pdf)

This sensor has 3 elements each being heated and consuming approximately 30mA. The sensor's resistance is measured and relates to chemical reduction (CO), oxidation (NOx), and NH3 concentration.

Nominal resistance for NH3 is 10-1500kOhm, for NO2 0.8 to 20kOhm and CO 100 to 1500kOhm. Factory calibration is needed to measure absolute values since the nominal resistance varies significantly for each sensor.

| Sensor | Nominal $R_{0_{min}} $ | Nominal $R_{0_{max}} $ | $C_{min}$ | $C_{max}$ | $R_S/R_0 min$ | $R_S/R_0 max$| low concentration
|---|---|---|---|---|---|---|---|
| CO| 100k| 1500k| 1ppm| 1000ppm| 4 | 0.01 | high resistance
| NH3| 10k| 1500lk| 1ppm | 300ppm| 0.08 | 30 | low resistance
| NOx| 0.8k| 10k| 0.05ppm | 10ppm| 0.8 | 0.07 | high resistance

The Amphenol sensor does not have an integrated analog to digital converted and the resistance will need to be measured using a resistor network such as a voltage divider. Its necessary to adjust a voltage divider for each sensor so that the maximum sensitivity is achieved with a microcontroller's internal ADC. It usually is more important to detect low quantities than to measure accurately high levels of the analyte. The ESP32 AD converter has an internal attenuator and the minimum accurate measurement is 0.1V and the maximum 2.4V. It requires linearization and averaging to obtain an accurate value. 

The example **heater** circuit in the datasheet of this sensor is for a 5V supply design and puts the CO and NH3 heater in series. For 3.3V operation, the heaters need to be connected independently, each with its own serial current limiting resistor. Current and nominal resistance of the heater can be obtained from the datasheet and the required serial resistor is as following:

| Gas | $I_{heat}$ [mA]| $R_{heat}$ [Ohm]| $V$ [V] | $R_{serial_{5V}}$ [Ohm]| $R_{serial_{3.3V}}$ [Ohm] |
|---|---|---|---|---|---|
| CO  | 32 | 74 | 2.4 | 82  | 29  |
| NOx | 26 | 66 | 1.7 | 126 | 61  |
| NH3 | 30 | 72 | 2.2 | 95  | 38  |

## Neopixel

To indicate status we use RGB LEDs controlled with 800kpbs serial signal. These LEDs come in different form factors usually 5x5mm but 1x1 and 2x2 are available with similar performance. Since each color can draw up to 5mA the current for one element is 15mA if white color is selected. With 12 LEDs and all emitting white, this would result in 200mA current consumption on the supply line. The serial signal is 3.3V compliant and the LED should work with 3.3V supply also, although 5V is recommended.
[datasheet](Airquality\datasheets\2301111010_XINGLIGHT-XL-2020RGBC-WS2812B_C5349955.pdf)

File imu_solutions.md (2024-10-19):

# Inertial Measurement Unit Solutions

## Breakout Boards
- [Sparkfun ICM20948](https://www.sparkfun.com/products/15335)
- [Adafruit ICM20948](https://learn.adafruit.com/adafruit-tdk-invensense-icm-20948-9-dof-imu)
- [Sparkfun ISM330DHCX & MMC5983MA](https://www.sparkfun.com/products/19895)
- [Sparkfun BNO086](https://www.sparkfun.com/products/22857)
- [Adafruit BNO055](https://www.adafruit.com/product/2472)

## Bosch

**BN055**
- Sensor Fusion
- Accel
    - 8Hz - 1kHz sampling rate
    - 2,4,8,16 g range
    - 3.4mg/C drift
    - 150 ug/sqrt Hz noise
- Gyro
    - 12-523 Hz sampling rate
    - 125 - 2000 degree/s range
    - 0.03 %/C drift
    - 0.014 degree/s / Hz noise
- Mag
    - 1300 micro T range

## TDK/Invensense

**ICM-20948**

- Sensor Fusion
- SPI
- 4k FIFO
- Accel
    - 4.5Hz -4.5kHz sampling rate
    - 2,4,8,16 g range
    - 0.8mg/C drift
    - 230 ug/Hz noise
    - 68.9 microA power consumption
- Gyro
    - 4.4Hz - 4.5kHz sampling rate
    - 250 - 2000 degree/s range 
    - 0.026 %/C drift
    - 0.015 degree/s / Hz noise
    - 1.23 mA power consumption
- Mag
    - 4900 uT range
    - 90 microA power consumption

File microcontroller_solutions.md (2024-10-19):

# Microcontroller

During development, **Adafruit ESP32-S3 Feather** was primarily used but also **SparkFun Thing Plus** to test an older hardware version that offers faster analog to digital conversion.

## ESP Variants

### ESP 8266
- released in 2014
- L106 32-bit RISC microprocessor core based on the Tensilica
- 32kBytes RAM
- IEEE 802.11 b/g/n Wi-Fi
- I2C, I2S, SPI
- Low quality A/D
- $3.50

### ESP32 
- released in 2016
- about 100 times faster than ESP8266
- Xtensa dual-core (or single-core) 32-bit LX6 microprocessor
- Wi-Fi: 802.11 b/g/n
- Bluetooth: v4.2 BR/EDR and BLE (shares the radio with Wi-Fi)
- I2C, SPI, I2S
- A2DP (Bluetooth Classic)
- Low quality A/D
- $5.50
  
### ESP32-C3
- released in 2020
- 32-bit RISC-V-based single-core
- 400kBytes
- Bluetooth Low Energy 21dB
- WiFi 2.4GHz 54Mbit/s
- 22 GPIO pins
- Low quality A/D
- Does not support A2DP (Bluetooth Classic)
- I2S performance might be low
- $6.50
  
### ESP32-S3
- released 2020
- Xtensa dual-core 32-bit, 240MHz
- 512kBytes
- Bluetooth Low Energy 20dB (smaller is better)
- WiFi 2.4GHz 54Mbit/s
- 45 GPIO pins
- Low quality A/D
- Does not supprt A2DP (Bluetooh Classic)
- Likely will BLE Audio will not be usable
- Arduino Library support for I2S is in beta
- Arduino-Audio-Tools does not support AudioStream?
- $11.50
  
### ESP32-C6
- released in 2023
- Arduino IDE support with ESP Arduino version 3.0 and later
- RISC-V dual core 32-bit 160MHz
- WiFi 6
- Bluetooth LE 5
- Zigbeee
- 8 Mbytes
- Has I2S peripheral
- $10

## Teensy Variants

### Teensy 4.x based
- ARM Cortex-M7 at 600 MHz
- I2C, SPI, I2S, Ethernet
- Precision A/D
- Fastest Microcontroller, about 7 x ESP32

### Teensy 4.0
- Micro USB
- 2Mbytes
- $23.80

### Teensy 4.1
- Micro USB
- FlashCard
- 8Mbytes
- $31.50

## Development Boards

### SparkFun Thing Plus - ESP32 WROOM
- USB type C  or micro
- Single Core
- 16Mytes SPI Flash
- Lipoly battery connector
- Built-in battery charging when powered over USB-C/micro
- STEMMA Q connector for i2c devices
- $24.95

### Adafruit ESP32-S3 Feather
- USB type C or Lipoly battery
- Built-in battery charging when powered over USB-C
- STEMMA Q connector for i2c devices
- $17.50

### Adafruit QT Py ESP32-S3 WiFi Dev Board with STEMMA QT
- USB type C
- STEMMA Q connector for i2c devices
- Tiny
- will not work with I2S (sound)
- $12.50

### Arduino Nano ESP32 (S3)
- USB-C
- $20

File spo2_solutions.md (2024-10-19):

# Pulseoximetery

## Electronic Designs

### Breakout boards
- [Protocentral Pulse Ox using TI AFE4490](https://protocentral.com/product/protocentral-afe4490-pulse-oximeter-breakout-board-kit/) $80

### Analog Front Ends

- **Texas Instruments**
    - [General](https://www.ti.com/solution/pulse-oximeter) 
    - [AFE4490 for clinical sensors](https://www.ti.com/lit/ds/symlink/afe4490.pdf?ts=1680618647641)

- **Analog Devices**
    - [General](https://www.analog.com/en/applications/markets/healthcare-pavilion-home/vital-signs-measurement/spo2.html)
    - [ADPD105](https://www.analog.com/en/products/adpd105.html) for clinical sensors 
    - [ADPD106](https://www.analog.com/en/products/adpd106.html) for clinical sensors
  
- **Maxim**
    - [MAX30101](https://www.maximintegrated.com/en/products/interface/signal-integrity/MAX30101.html), fully integrated, does not allow connecting to clinical sensor
    - [MAX86180](https://www.analog.com/en/products/max86180.html), driver for 8 external LEDs and 8 photodiodes

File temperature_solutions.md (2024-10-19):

# Thermistors

Example suppliers for medical grade thermistors are: 

- Amphenol
    - [General](https://www.amphenol-sensors.com/en/product-spotlights/3468-temperature-sensing-for-medical-devices)
    - [MA100BF103AN or MA100GG103AN](https://www.mouser.com/datasheet/2/18/Amphenol_04022020_AAS_920_321E-1826352.pdf)

- Smith Medical / icumedical
    - [Probes](https://www.icumed.com/products/temperature-management/?line=temperatureprobes)

- Variohm
    - [Probes](https://www.variohm.com/products/temperature-sensors)

# ICS with integrated thermistor 
- [Max30205](https://www.analog.com/media/en/technical-documentation/data-sheets/max30205.pdf)
- [Protocentral MAX30205](https://protocentral.com/product/protocentral-max30205-body-temperature-sensor-breakout-board/)

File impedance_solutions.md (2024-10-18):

# Impedance Solutions 

## IEC 60601 
IEC 60601 limits 100 µA maximum dc-leakage current through the body under normal conditions and 500 µA maximum under worst-case, single-fault conditions. An impedance circuit should not exceed that current.

## Analog Devices AFE
- [AD5933 12-bit impedance converter ($18)](https://www.analog.com/en/products/ad5933.html) evaluation kit available ($68)
- [User Guide with reference schematics](https://www.analog.com/media/en/technical-documentation/user-guides/UG-364.pdf)

## Maxim AFE
- Biopotential
  - ECG (waveform)
  - R-R (heart rate)
- Bioimpedance
  - Resp (respiration)
  - GSR (galvanic skin response, stress level)
  - EDA (electro dermal activity)

- [Max 30001G ($10)](https://www.maximintegrated.com/en/products/analog/data-converters/analog-front-end-ics/MAX30001G.html) for Biopotential and Bioimpedance, evaluation kit available ($113)
- [Maxim 30009](https://www.maximintegrated.com/en/products/sensors/MAX30009.html) for Bioimpedance, evaluation kit available ($212)

## AFE Summary

| PART | Features             | Resolution | Remarks |
|---   |---                   |---         |---      |
|AD5933|Single channel 3 wire | 12bit, 1Msps, 100kHz excitation| First Gen, 1024 point FFT, 1kOhm - 1MOhm
|AD5940/41 | 2 channel, 4 wire | 16bit, 800ksps, 200kHz | Impedance spectroscopy
|ADuC355 | 2 channel, 4 wire | 16bit, 800ksps, 200kHz | Impedance Spectroscopy, 26MHz ARM Cortex M3 MCU
| MAX30002 | single channel, BioZ, 2 or 4 wire | 17bit| 
| MAX30009 | single channel, BioZ, 2 or 4 wire | 16 kHz - 806 kHz |
| MAX30131/132/134 | 1-,2-,4- channel | 12 bit |
| MAX30001G | single channel, 2 or 4 wire | BIOZ: 1-100kHz xx bit, ECG: xxbit | Impedance and Potential (ECG)

## References

For general reading: [Analog Devices: Bio-Impedance Circuit Design for Body Worn Systems"](https://www.analog.com/en/resources/analog-dialogue/articles/bioimpedance-circuit-design-challenges.html)

1) [Analog Devices AD5933 Evaluation Board, User Guide](https://www.analog.com/media/en/technical-documentation/user-guides/UG-364.pdf)
2) [Munoz et a, 2022, A low-cost, portable, two-dimensional bioimpedance distribution estimation system based on the AD5933 impedance converterl](https://doi.org/10.1016%2Fj.ohx.2022.e00274)
3) [AD5933 Datasheet](https://www.analog.com/media/en/technical-documentation/data-sheets/AD5933.pdf)
4) [Instructables: Body Composition](https://www.instructables.com/Determining-Body-Composition-using-Arduino)
5) [Instructables: BIA 1](https://www.instructables.com/Body-Composition-using-BIA/)
6) [Instructables: BIA 2](https://www.instructables.com/Bio-Impedance-Analysis-BIA-With-the-AD5933/)
7) [Instructables: Thor 1](https://www.instructables.com/Thoracic-Impedance-1/)
8) [Instructables: THor 2](https://www.instructables.com/Thoracic-Impedance/)

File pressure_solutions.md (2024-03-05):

# Pressure

## Example pressuer ranges
- systolic > 140mmHg  maximum 0.25bar
- diastolic 60-80mmHg minimum: 0.05bar
- lung 300cm H2O -170cm H2O -0.5bar .. 0.75bar

# Sparkfun
- SparkFun Qwiic MicroPressure Sensor
- Several sensors available, need to check range, noise and smallest measurable pressure change

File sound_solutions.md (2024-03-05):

# Sound Recording

## Digital Stethoscope

- [IEEE Paper with Arduino](https://ieeexplore.ieee.org/document/8994674)

## Audio Library for Arduino and ESP
- [arduino-audio-tools](https://github.com/pschatzmann/arduino-audio-tools) with [audiotools review](https://youtu.be/a936wNgtcRA?si=jpXgP3CTCKrXq8GU)
- [arduino-audio-driver](https://github.com/pschatzmann/arduino-audio-driver)

## Sound Codecs
Suggested codecs to work with micro controllers.

- [SGTL5000, NXP](https://www.nxp.com/products/audio-and-radio/audio-converters/ultra-low-power-audio-codec:SGTL5000)
- [ES8388, Everest Semidoncutors](https://pcbartists.com/wp-content/uploads/2022/07/ES8388-module-datasheet-July-2021.pdf)
- [VS1053, VLSI Solution](https://cdn-shop.adafruit.com/datasheets/vs1053.pdf)
- [WM8960, NXP](https://community.nxp.com/pwmxy87654/attachments/pwmxy87654/imx-processors/52419/1/WM8960.pdf)
  
## Sound boards
Sound boards developed for micro controllers, using i2s:

- [Teensy audio board (SGTL5000)](https://www.pjrc.com/store/teensy3_audio.html) $14.40
- [Audiopants ESP32 based on Teensy Audio (SGTL5000)](https://noties.space/headphones-help), [Audiopants github](https://github.com/chipperdoodles/audiopants)
- [audioinjector](https://www.audioinjector.net/) Produces several audio boards for raspberry pi. They likely also work for micro controllers.
- [I2S ADC Audio I2S Capture Card Module](https://github.com/pschatzmann/arduino-audio-tools/wiki/External-ADC#i2s-adc-audio-i2s-capture-card-module) $12
- [ES8388 Audio Codec Module](https://github.com/pschatzmann/arduino-audio-tools/wiki/Audio-Boards#es8388-audio-codec-module) $17
- [VS1053 Audio Codec Modules](https://github.com/pschatzmann/arduino-audio-tools/wiki/Audio-Boards#vs1053-audio-codec-modules) $5
- [PI WM8960 Hat](https://github.com/pschatzmann/arduino-audio-tools/wiki/Audio-Boards#pi-wm8960-hat) $16
   
## Microphone Amplifier breakout board
- [Sparkfun](https://learn.sparkfun.com/tutorials/sound-detector-hookup-guide) with [LMV321](http://cdn.sparkfun.com/datasheets/Sensors/Sound/LMV324.pdf) $12
- [Adafruit MAX9814](https://www.adafruit.com/product/1713) $8

## Regular Microphones 

They need an amplifier and a ADC.

| Model | Sensitivity dB | SNR dB |
| ----- | ----------- | --- |
| [PUI Audio AOM-5244L-HD-R (just mic)](https://puiaudio.com/product/microphones/AOM-5244L-R) | -44 | 60 | 
| [PUI Audio AOM-5054 (jsut mic)](https://puiaudio.com/products/anm-5054l-2-r)      | -54 | 55 | 

## Regular MEMS Microphones 

They need an amplifier and an ADC.

| Model | Sensitivity dB | SNR dB SBL | SNR dB A
| ----- | ----------- | --- | --- |
| [Knowles MQM-32325](https://www.knowles.com/docs/default-source/model-downloads/mqm-32325-000.pdf) | -58 | 26.5 |
| [Knowles MM25-33663](https://www.knowles.com/docs/default-source/default-document-library/mm25-33663-000.pdf) | -57 | 25 | 69
| [PUI Audio AMM-3742](https://puiaudio.com/product/microphones/amm-3742-t-r) | -42 | | 58 |
| [PUI Audio AMM-2742](https://puiaudio.com/product/microphones/AMM-2742-T-R) | -42 | | 59 |

Knowles KAS-33100-003 Evaluation Kit uses Cirrus Logic Stereo Codec. Interfaces with USB to PC and not to microcontroller though.
Can also use SparkFun Analog MEMS Microphone Breakout - ICS-40180 for amplification but still need ADC for digital conversion.

## I2S MEMS Microphones
MEMS are small and require low power.

| Model                 | Sensitivity dB FS | SNR dbA | Equivalent Noise dBA | Dyanmic Range dB |
| --------------------- | ----------- | ------ | ---------------- | ------------- |
| Knowles SPH0645LM4H-B | -26 | 65 | 33 | |
| TDK/InvenSense ICS-43434 | -26 | 65 | 29 | 91 |
| TDK/InvenSense INMP 441 | -26 | 61 |
| Analog Devices ADMP441 obsolete| -26 | 65 | | |
| STMicroelectronics MP34DT05-A | -26 | 64 | | |

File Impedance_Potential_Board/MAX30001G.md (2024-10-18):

# MAX 30001G

Here we summarize the features and design consideration of the MAX 30001G. This should shorten the read of the datasheet.

**ECG/Biopotential:** 
Common Mode Rejection is 100dB. Noise is $4.6\mu V_{p-p}$ at $0.05-150Hz$ bandwidth. It sues a  18bits ADC at 125-512 samples per second. Built in digital highpass ($0.5Hz$) and lowpass ($40$, $100$ or $150Hz$) filter as well as R-R time measurement unit for heart reate measurement.

**Impedance:**
Uses a square wave generator with $100nA$ or $8-96 \mu Amp$ operating at $0.125-131kHz$. The ADC operates 20bits and 25-64 samples per second. Noise is $1.1 \mu V_{p-p}. Output digital filters are available to create a low pass at $4$, $8$ or $16Hz$ and a high pass at $0.05$ or $0.5 Hz$.

SPI communication can occur at >0-12MHz.

The device operates on 1.8V and can produce 3.3V digital output signals for SPI as well as interrupts.

This chip comes only in Waver Level Packing [WLP] which has a 0.5mm pad pitch and a 0.25mm pad size. This results in highest level of difficulty for soldering as alignment will need to be at 0.1mm.

## MAX 30001G ECG Channel

The ECG channel consist of an input MUX to switch between leads, instrumentation amplifier, anti alias filter (3dB at 600Hz) for ADC and a programmable gain amplifier. The input MUX has ESD protection and EMI filtering and can detect wether leads are on or off. CAPP and CAPN provide external capacitor connection to set the amplifiers' low pass filter. Other functions are enabled internally.

The is leads-off detection while measuring and leads-on detection while the ECG channel is powered down. For leads-on detection a selectable current 0-100nA is applied to the leads and if the voltage is below a threshold for more than 140ms, the off conditions is met. When impedance between ECGP and ECGN is less then 40M Ohm a leads-on interrupt is triggered.

Common mode between ECGP and ECGN should not exceed 550mV when the chip is run at 1.8V. This can be achieved with internal lead biasing. Optionally, VCM can be connected with a third electrode to the body to create common voltage on the skin surface.

Calibration voltage sources are available to calibrate the ECG channels at $0.015 - 256 Hz$ and $+/-0.25$ or $0.5mV$ amplitude.

A high pass filter can be attached to CAPP and CAPN which results in a low pass frequency of $f_c = 1 / (2 \pi R C)$ where R is approximately $450k Ohm$. If C is $10\mu F$ $f_c$ is $0.035 Hz$.

The built in anti aliasing filter is a 2 pole active filter with f_c at 600Hz.

The instrumentation amplifier has a GAIN register.

Before ADC the signal is amplified by 1, 2, 4 or 8 resulting in total amplification of $20$, $40$, $80$ or $160$ V/V.

The converted data is 18 bit left justified two's complement. After converting to signed magnitude one obtains the actual signal with 

$V_{ECG}=ADC*V_{REF}*/2^{17} * ECG_{GAIN}$ 

where $V_{REF}$ is typically $1000mV$.

At 512 samples per second the output latency is $20-32 ms$ where as $32ms$ represents the condition when the digital low pass filter is engaged.

R-R detection is possible with Pan-Tompkins QRS detection algorithm. Timing accuracy is about 8ms. The latency of the algorithm is about 100 ms.

## MAX 30001G BioZ Channel

The bio impedance channel consists of a driver and an input chain. The input mux measures the two input electrodes with a multiplexer and provides ESD and EMS protection. It can also detect leads-on and off condition.  The signal passes a high pass filter followed by an amplifier and is then demodulated with the driver signal at a selectable phase offset. After an anti-aliasing filter at 600Hz the signal is converted to digital.

There are 3 methods to detect leads off. 

The compliance to generating current in the driver is monitored and triggered when voltage is out of expected range (enabled with BIOZ_CGMON). 

There is lead-off detection on the BIP and BIN leads operating the same way as in ECGP and ECGN.

Common Mode on BIP and BIN is limited to 550mV when operating the chip at 1.8V. Internal bias can be applied to BIP and BIN or VCM can be used to generate common mode on the skin.

Calibration voltage sources similar to the ECG cahnnel are available.

Internal calibration resistors are available for DRVP and DRVN to test driver functionality.

The current generator on DRVP and DRVN is a square wave modulation that is AC injected in to the body. In high current mode $8-96\mu A$ we need to attach a 324k Ohm resistor to $R_{BIAS}$. Both active and resistive common mode feedback is available. Current injection frequencies are 125Hz to 132kHz. A programmable resistor is used to adjust the injected current.

ADC operates at 20 bits and results in a left justified two's complement number. After signed magnitude conversion,

$BioZ = ADC x V_{REF} / (219 x BIOZ_{CGMAG} x BIOZ_{GAIN})$ in [Ω].

$V_{REF}$ typically is 1V.  $BioZ_{CGMAG}$ is $50 nano$ to $96 \mu A$ and $BIOZ_{GAIN}$ is $10$, $20$, $40$, or $80V/V$.

## Computing and Configuring Impedance

To calculate the body impedance, one needs to analyze all electrical components in the network. An electrode model should be used for example Model 1 mentioned above with values from the MAX datasheet.

### 2 Lead Measurement

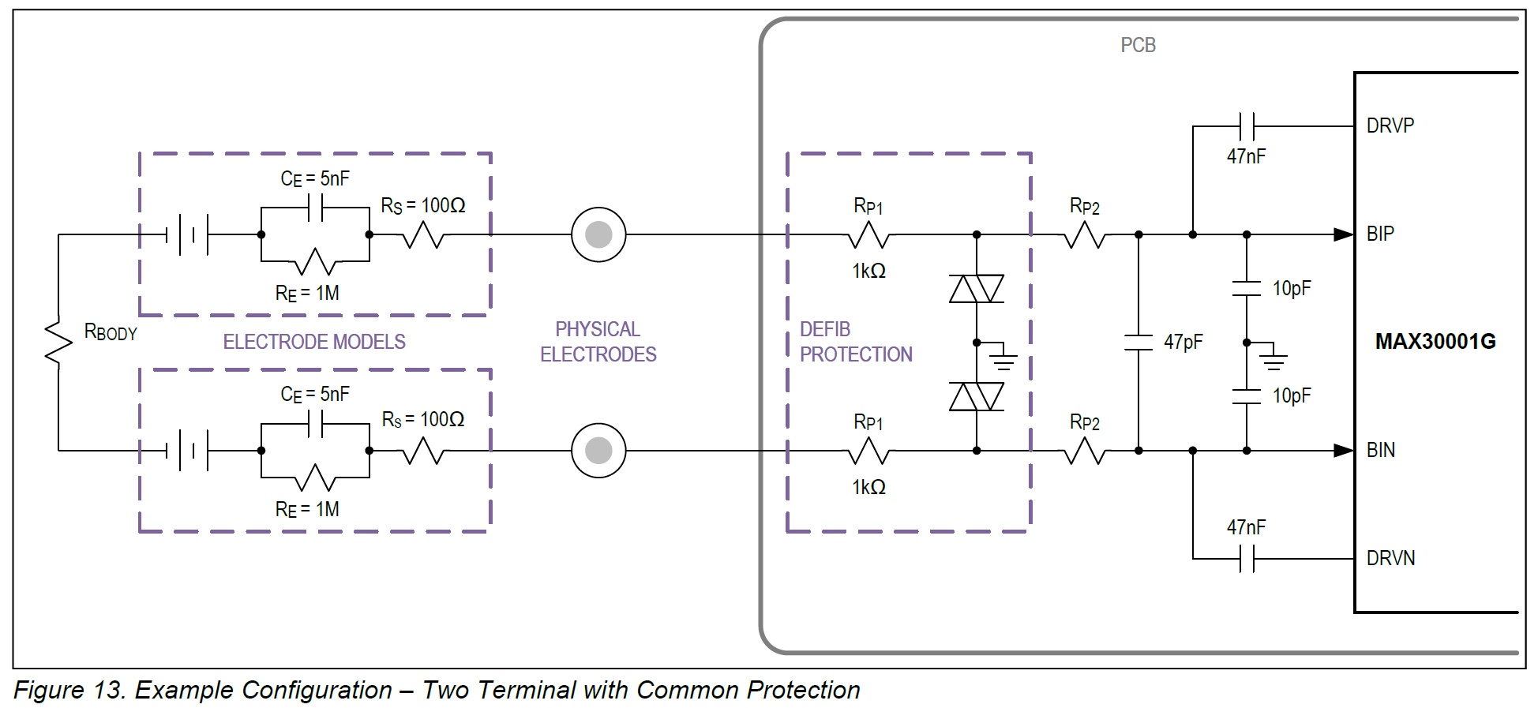
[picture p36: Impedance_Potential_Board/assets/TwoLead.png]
Two Lead

(from MAX30001G data sheet)

DRVP and DRVN are connected to BIN and BIP with $0.47nF$ capacitors (close jumpers DN-BN and DP-BP in our design). (Need to change design to match capacitors). BIN and BIP have default capacitors attached: 10pF and 47pF.

The total impedance on BIP and BIN is:

$R_{BODY} + 2 R_{P1} + 2 R_{P2}+ 2 R_S + Re (2R_E * 1 / (1+jωR_E C_ E))$

Where Re is the real part and is:

$2R_E * 1 / (1+(ωR_E C_ E)^2)$ 

with $ω = 2 \pi f$

In our design $R_{P1}$ and $R_{P2}$ are 0. At 80kHz $R_{BODY}$ is about 100 Ω and therefore the equation above results in and impedance of about 300 Ω (C_E and R_E are negligible).

The maximum current injection is the maximum AC input differential range ($90mV_{peak}$) divided by the network impedance (300 Ω) or 300 micro Amp. The closes selectable current the system can generated is $96 \mu A_{peak}$.

### 4 Lead Measurement

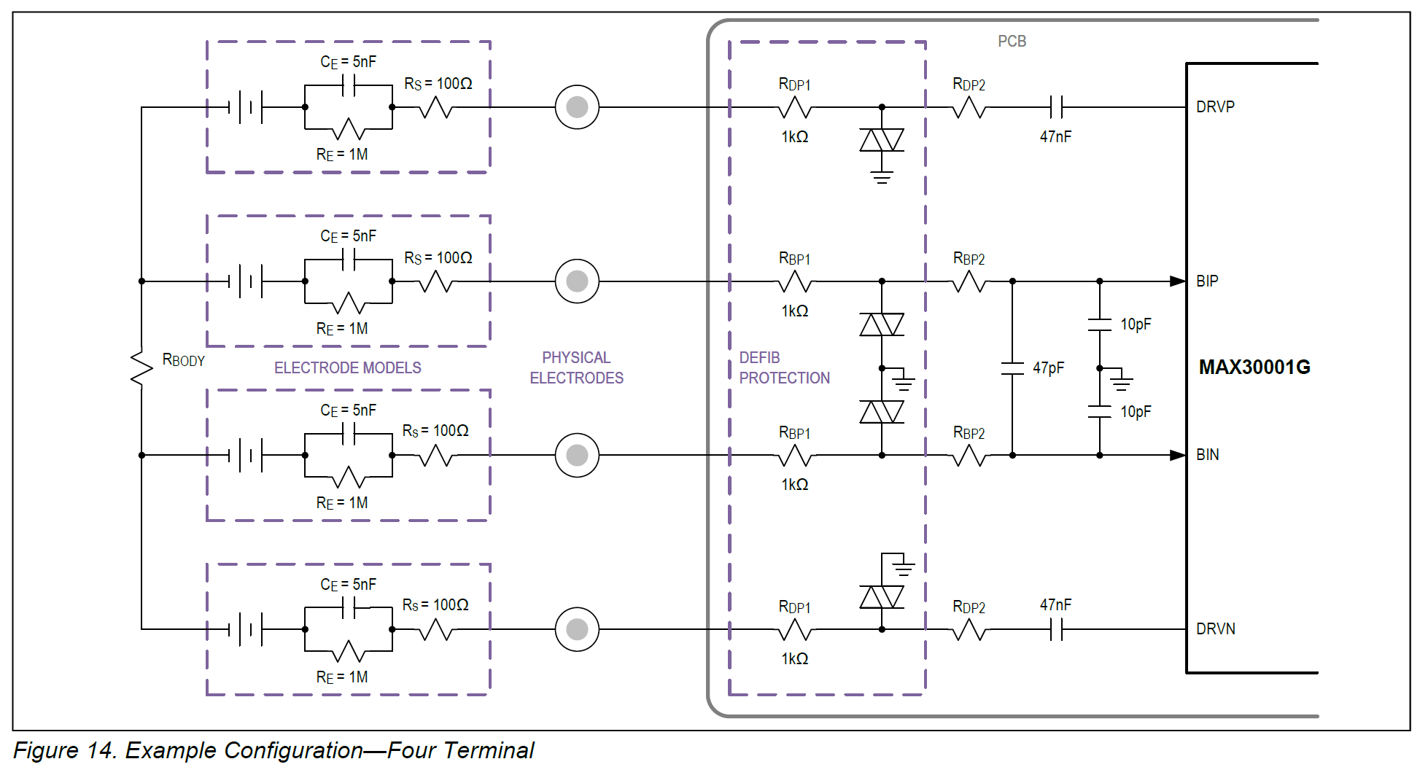
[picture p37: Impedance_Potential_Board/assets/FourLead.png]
Four Lead

(from MAX30001G data sheet)

There is no difference in calculating the real part of the impedance on BP and BN.

The maximum current for injection is the DRVP DRVN compliance voltage (VDD-0.5V = 1.1V for VDD = 1.8V) divided by the network impedance ($300 Ω$) or $4.3mA$. The closest selectable current is again $96 \mu A_{peak}$.

### Rest of circuit

The high-pass filter options include a fourth-order IIR Butterworth filter with a $0.05Hz$ or $0.5Hz$ corner frequency along with a pass through setting for DC coupling.

Low pass filter options include a 12-tap linear phase (constant group delay) FIR filter with $4$, $8$, or $16Hz$ corner frequencies.

The shortest latency is $100ms$ without filter and $200ms$ with filter.

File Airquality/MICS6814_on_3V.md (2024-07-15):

# MiCS 6814
The datasheet of the MiCS6814 shows a simplified circuit diagram for 5V operation where the CO and NH3 sensor are connected in series to the power supply for a simpler circuit. We do not use that circuit.

The internal connections of the sensor are illustrated here.
The horizontal connection is the heater and vertical is the sensor. The sensors are read with a voltage divider and the curret for the heater is limitted through a resistors conencted in series.



If you look at the [PIMORONI sensor](https://shop.pimoroni.com/products/mics6814-gas-sensor-breakout?variant=39296409305171) schematic, you will see that some of the connections are inverted. For example E and C are flipped as well as F and D.

For 3.3V operation I computed the heater serial resistor as following:

| Element | Voltage [V] | Current [A] | Power [W] | $R_{pre}$ [Ohm]
| ---     | ---         | ---         | ---       | ---
| $CO$    | 2.4         | 0.032       | 0.076     | **28.1**  
| $NO_x$  | 1.7         | 0.026       | 0.042     | **61.5**
| $NH_3$  | 2.2         | 0.030       | 0.066     | **36.6**

- $CO$ Heater: $(3.3[V]-2.4[V])/.032[A] = 28.1 [Ohm]$

- $NO_x$ Heater: $(3.3[V] - 1.7[V])/0.026[A] = 61.5[Ohm]$

- $NH_3$ Heater: $(3.3[V] - 2.2[V])/0.03[A] = 36.6[Ohm]$

## Sensing Voltage Divider

The sensors have a large variation of basline resistance after they are manufactured. The sensor sensitivity is also varying over an oder of manitude. Therefore its difficult to predict an appropriate resistor.

Ideally the sensor is operated in a clean environment and the sensor resistance is measured and then the voltage divider resistors are adjusted so that we have best readings at low concentrations. One optioin is to choose the voltage divider resistor so that is has the same value as the sensor in clean air. 

Using the circuit above and the data sheet:
- The CO reading will decrease if concentration increases.
- The NO_x reading will increase if the concentration increases.
- The NH_3 reading will decrease if concentration increases.

### Sensor Response

From the graphs on the data sheet we can calculate the values the sensor resistor might be at small and large gas concentrations. The graphs show only one possible sensitivity.

|Gas    |Conc [ppm] | $R/R_0$ | $R_s$ min | $R_s$ max 
|---    |---        | ---     | ---       | ---
|$CO$   | 1         | 3.2     | 320k      | 4800k
|$CO$   | 1000      | 0.01    |   1k      |   15k

$R_0$ max = 1500k
$R_0$ min = 100k

The carbon monoxide sensor is also responding to Hydrogen, Ethanol and Ammonia.

|Gas    |Conc [ppm] | $R/R_0$ | $R_s$ min | $R_s$ max
|---    |---        | ---     | ---       | ---
|$NO_2$ | 0.01      | 0.06    |  48       | 1.2k
|$NO_2$ | 6         | 40      |  32k      | 800k

$R_0$ max = 20k
$R_0$ min = 0.8k

The NO_x sensor is weakly responding to NO and Hydrogen.

|Gas    |Conc [ppm] | $R/R_0$ | $R_s$ min | $R_s$ max
|---    |---        | ---     | ---       | ---
|$NH_3$ | 1         | 0.8     | 8k        | 1200k
|$NH_3$ | 100       | 0.065   | 650       | 97.5k

$R_0$ max = 1500k
$R_0$ min = 10k

The NH_3 sensor also responds to Ethanol, Hydrogen, Propane and Iso-butane.

For CO the resistor should be between 320k and 4.8M Ohm. (1.2M selected)

For NO2, the resistor sould be between 48 and 1.2k Ohm. (30k selected)

For NH3, the resistor should be between 8k and 1200k Ohm. (47k selected)

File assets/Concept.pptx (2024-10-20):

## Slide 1

Signal
Conditioning

A/D
I2C

ESP32-S3

BLE Receiver

Battery

Display and Storage

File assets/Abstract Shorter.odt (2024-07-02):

BMES 2024 Abstract

Open source platform to measure physiological signals in a classroom setting

Urs Utzinger 1,2

Carmella Ocaya 1, mcocaya@arizona.edu

Muad Alsayar 2, moathalsayyar@arizona.edu

Alec Newman 3, wmalecnewman@arizona.edu

Daniel Campana 2, grender007@arizona.edu

Michael Morrett 3, michaelmorrett@arizona.edu

1 Department of Biomedical Engineering,

2 Department of Electrical and Computer Engineering,

3 Department of Aerospace and Mechanical Engineering

4 Department of Biosystems Engineering

The University of Arizona

## Introduction

To complete their education, biomedical engineering undergraduate students must measure and interpret data from living systems[1]. One approach to achieve this learning goal, is to record data from normal volunteers in a classroom setting. Inexpensive equipment is needed that can safely record common physiological signals. While there are commercial systems available [2] [3], there is no approach that uses an open hardware design and gives the option to expand functionality at later time. We present an example solution that can be produced in most academic settings using commonly available electronic and additive manufacturing techniques. An advantage of such a solution is that its data recording and computing components support programming courses and the measurement modules can also serve academic research projects.

## Material and Methods

The system consists of several independent modules, a charging station and a base station. The modules as well as the base station contain an ESP32 micro controller. The modules transmit data to the base station using the ESPNow protocol. All modules are battery operated using lithium ion battery. Common ESP32 platforms connect to custom electronics boards. The boards contain analog front ends and interface with standard biomedical sensors. The components are mounted in a 3d-printed housing.

The system uses micro controllers to communicate wirelessly with a data recorder. It uses common protocols to control and record data. All systems are battery operated to electrically isolate the sensor modules from building ground. Open source software is used to develop micro controller instructions (Arduino IDE [4] and display and record data (Python [5]). To develop custom electronic circuits we used Eagle CAD (Autodesk) which is available freely when designing two layer printed circuit boards. For mechanical designs, Solidworks (Dassault Systems) and OnShape (PTC Inc) was used. Solidworks is available through academic licensing and OnSahpe offers free education accounts.

Custom electronic boards were manufactured by PCBWay (PCB assembly service).

Most components were designed as part of a senior capstone project in the college of engineering at the University of Arizona.

For manufacturing, soldering equipment and a 3d-pinter is needed. Electronic wiring and component assembly requires soldering of through hole components. Programming requires a regular desktop or notebook computer.

## Results

All design files and software for this project are available on Github [6].

Analog front ends and analog measurement electronics were selected to record the following physiologic signals:

- Temperature

- Electric Potential (e.g. electro cardiogram or electro myogram)

- Electric Impedance

- Optical Transmission (e.g. plethysmogram or blood oxygenation)

- Physical activity (e.g. inertial measurement)

- Sound (e.g. heart or lung sounds)

- Pressure

A module to measure air quality parameters was also developed. Further modules are under development such as an air flow sensor module to measure lung functions.

For temperature measurements a medical grade temperature sensor (Amphenol, NTC Therrmistor) is connected to Wheatstone bridge. The micro controller’s internal analog to digital unit converts the voltage differential to resistance. The Steinhart-Hart equation is used to produce temperature readings. An error of less than 0.1 degrees C was achieved in the 0-50 centigrade range.

Sounds are recorded with a modified stethoscope that is connected to a microphone. The frequency range and amplification of an amplifier was adjusted to match the expected sound levels. An audio codec (ES8366) produces the digital readings. Reducing the sampling rate and dynamic range allows transmitting the data with the ESPNow protocol. Arduino-audio-driver and Arduino-audio-tools [7] allowed for efficient programming.

To create a blood pressure module the sound sensor was combined with an air pressure sensor (Honeywell, MPR Series) that can be connected to an arm cuff.

For bio potential and and bio impedance recordings a custom circuit for the MAX30001G (Maxim Integrated) was created. It allows monitoring ECG and respiration.

For pulse oximetry the AFE4490 (Texas Instruments) was used, allowing to connect reusable finger clip sensors that use a DB9 connector.

For activity measurements, the inertial measurement unit ICM20948 (TDK Invensense) and the barometric pressure sensor BMP581 (Bosch) were integrated into a sensor module.

The cost for each module varies and depends on the quantity ordered through the assembly service. An estimated cost for the assembled PCBs, housing and auxiliary parts for six different senor modules is in the range of $500-$1000.

## References

[1] ABET Accreditation Criteria, Program Criteria for Bioengineering and Biomedical and Similarly Named Engineering Programs, Citerion d, "Making measurements on and interpreting data from living systems", Biomedical Engineering Society.

[2]: Bioradio, https://staging.glneurotech.com/product-category/bioradio-all

[3]: Protocentral https://protocentral.com

[4]: https://www.arduino.cc/en/software

[5] https://www.python.org/

[6] https://github.com/uutzinger/BioMedicalSensorBoard

[7] https://github.com/pschatzmann

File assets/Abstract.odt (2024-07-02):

BMES 2024 Abstract

Open source platform to measure physiological signals in a classroom setting

Urs Utzinger 1,2

Carmella Ocaya 1

Muad Alsayar 2

Alec Newman 3

Daniel Campana 2

Michael Morrett 3

1 Department of Biomedical Engineering,

2 Department of Electrical and Computer Engineering,

3 Department of Aerospace and Mechanical Engineering

4 Department of Biosystems Engineering

The University of Arizona

## Introduction

To complete their education, biomedical engineering undergraduate students must measure and interpret data from living systems[1]. One approach to achieve this learning goal, is to record data from normal volunteers in a classroom setting. Inexpensive equipment is needed that can safely record common physiological signals. While there are commercial systems available [2] [3], there is no approach that uses an open hardware design and gives the option to expand functionality at later time. For a wide adoption, such equipment should be cost-effective. We present an example solution that can be produced in most academic settings using commonly available electronic and additive manufacturing techniques. An advantage of such a solution is that its data recording and computing components support programming courses and the measurement modules can also serve academic research projects.

## Material and Methods

The design requirements of our system are that it

- measures several common physiological signals

- can be easily reproduced at an educational institution

- records, displays and stores measurements safely in a class room setting

The system uses micro controllers to communicate wirelessly with a data recorder. It uses common protocols such as inter integrated circuit (I2C), serial peripheral interface (SPI) , inter-IC sound (I2S) to control and record data with integrated circuits. All system are battery operated to electrically disconnect sensor modules from building ground. 3D printing is used to manufacture component housings. Open source software is used to develop micro controller instructions (Arduino IDE [4] ) and display and record data (Python [5]). To develop custom electronic circuits we used Eagle CAD (Autidesk) which is available freely when designing two layer printed circuit boards. For mechanical design Solidworks (Dassault Systems) and OnShape (PTC Inc) was used. Solidworks is available through academic licensing and OnSahpe offers free education accounts.

Custom electronic boards were manufactured by PCBWay (PCB assembly service).

Most components were designed as part of a senior capstone project in the college of engineering at the University of Arizona.

For manufacturing, soldering equipment and a 3d-pinter is needed. Electronic wiring and component assembly requires soldering of through hole components. Programming requires a regular desktop or notebook computer.

## Results

All design files and software for this project is available on Github [6].

The system consists of several independent modules, a charging station and a base station. A module as well as the base station contain an ESP32 micro controller. The modules transmit data to the base station using the ESPNow protocol. All modules are battery operated using lithium ion battery. Common ESP32 platforms such as the Adafruit ESP32-S3 Feather or Sparkfun Thing Plus – ESP32-S3 are used to connect to custom expansionism boards. The expansion boards contain analog front ends and support electronics to interface with standard biomedical sensors. The components are mounted in a 3d-printed housing.

Analog front ends and analog measurement electronics were selected to record the following physiologic signals:

- Temperature

- Electric Potential (e.g. electro cardiogram or electro myogram)

- Electric Impedance

- Optical transmission (e.g. plethysmogram or blood oxygenation)

- Physical activity (e.g. inertial measurement)

- Sound (e.g. heart or lung sounds)

- Pressure

A module to measure air quality parameters was also developed. It records CO2 concentration, particulate matter density, environmental temperature and pressure as well as methane, volatile organic compounds. Further modules are under development such as an air flow sensor module to measure lung functions.

For temperature measurements a medical grade temperature sensor ()Ampheno, NTC Therrmistor) is connected to Wheatstone bridge measurement circuit. Two voltages are recorded using the micro contoller’s internal analog to digital converter. The measured differential is converted to thermistor resistance. The Seinhart-Hart equation is used to convert the readings to temperature. An error of less than 0.1C was achieved in the 0-50 centigrade range.

Sounds are recorded with a modified stethoscope that is connected to a microphone. The frequency range and amplification of an amplifier was adjusted to match the expected sound levels. An audio codec (ES8366) produced the digital readings. Reducing the sampling rate and dynamic range allows transmitting the data with the ESPNow protocol. Arudino-audio-driver and Arduinoaudio-tools [7] allowed for efficient programming.

To incorporate the sound sensor into arm cuff blood pressure sensor, an air pressure sensor (Honeywell, MPR Series) was integrated into the sound module.

For biopotential and and bio impedance recordings a custom circuit for the MAX30001G (Maxim Integrated) was created. It allows monitoring ECG and respiration but can measure impedance and electrical signals over a wide range.

For pulse oximetery the AFE4490 (Texas Instruments) was used in a custom PCB allowing to connect reusable finger clip sensors that use a DB9 connector.

For activity measurements the inertial measurement unit ICM20948 (TDK Invensense) and the barometric pressure sensor BMP581 (Bosch) are used.

The cost for each module varies and depends on the quantity ordered through the assembly service. An estimated cost for the assembled PCBs, housing and auxiliary parts for six different senor modules is in the range of $500-$1000.

## Conclusion and Discussion

A cost-effective measuring platform was developed that uses medical grade sensor. The design was optimized to meet safety requirements and commonly available manufacturing capabilities. Open source or freely available software is needed to program the sensor modules and record the data. For assembly the user will need to place a PCB assembly service request to a manufacturer, 3d-print the housing and solder wires to connect the micro controller board and the sensor board. State of the art components and modules were selected for the design of the system.

## References

[1] ABET Accreditation Criteria, Program Criteria for Bioengineering and Biomedical and Similarly Named Engineering Programs, Citerion d, "Making measurements on and interpreting data from living systems", Biomedical Engineering Society.

[2]: Bioradio, https://staging.glneurotech.com/product-category/bioradio-all

[3]: Protocentral https://protocentral.com

[4]: https://www.arduino.cc/en/software

[5] https://www.python.org/

[6] https://github.com/uutzinger/BioMedicalSensorBoard

[7] https://github.com/pschatzmann

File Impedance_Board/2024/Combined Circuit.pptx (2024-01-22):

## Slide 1

Analog Devices Evaluation Board

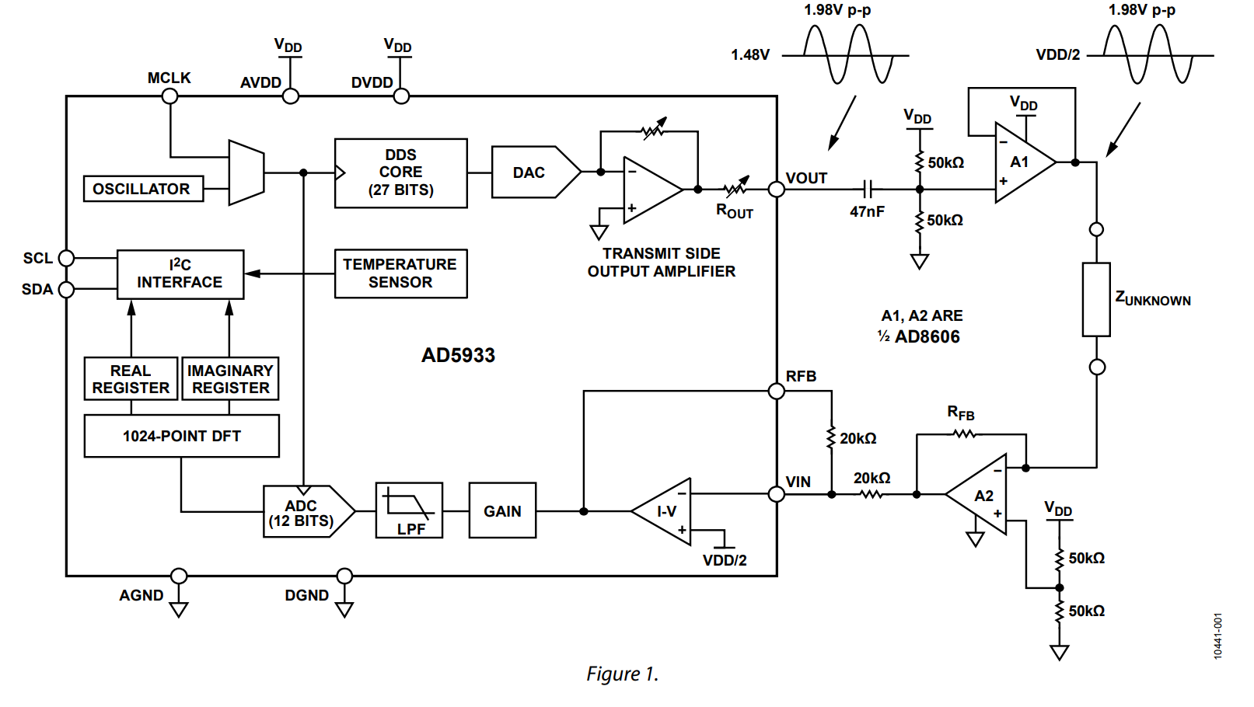
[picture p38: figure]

Analog Devices Evaluation Board

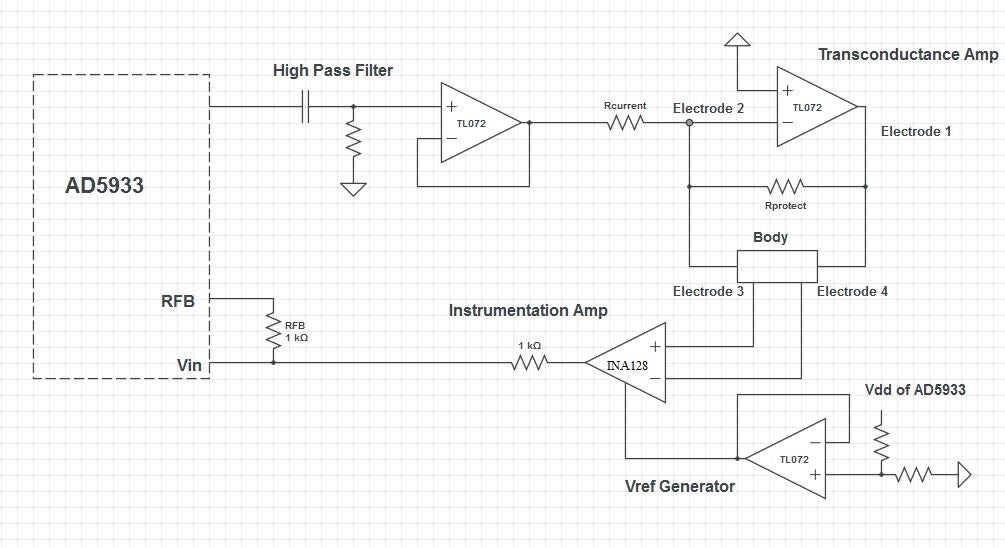
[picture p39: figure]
Determining Body Composition Using Arduino

Instructables

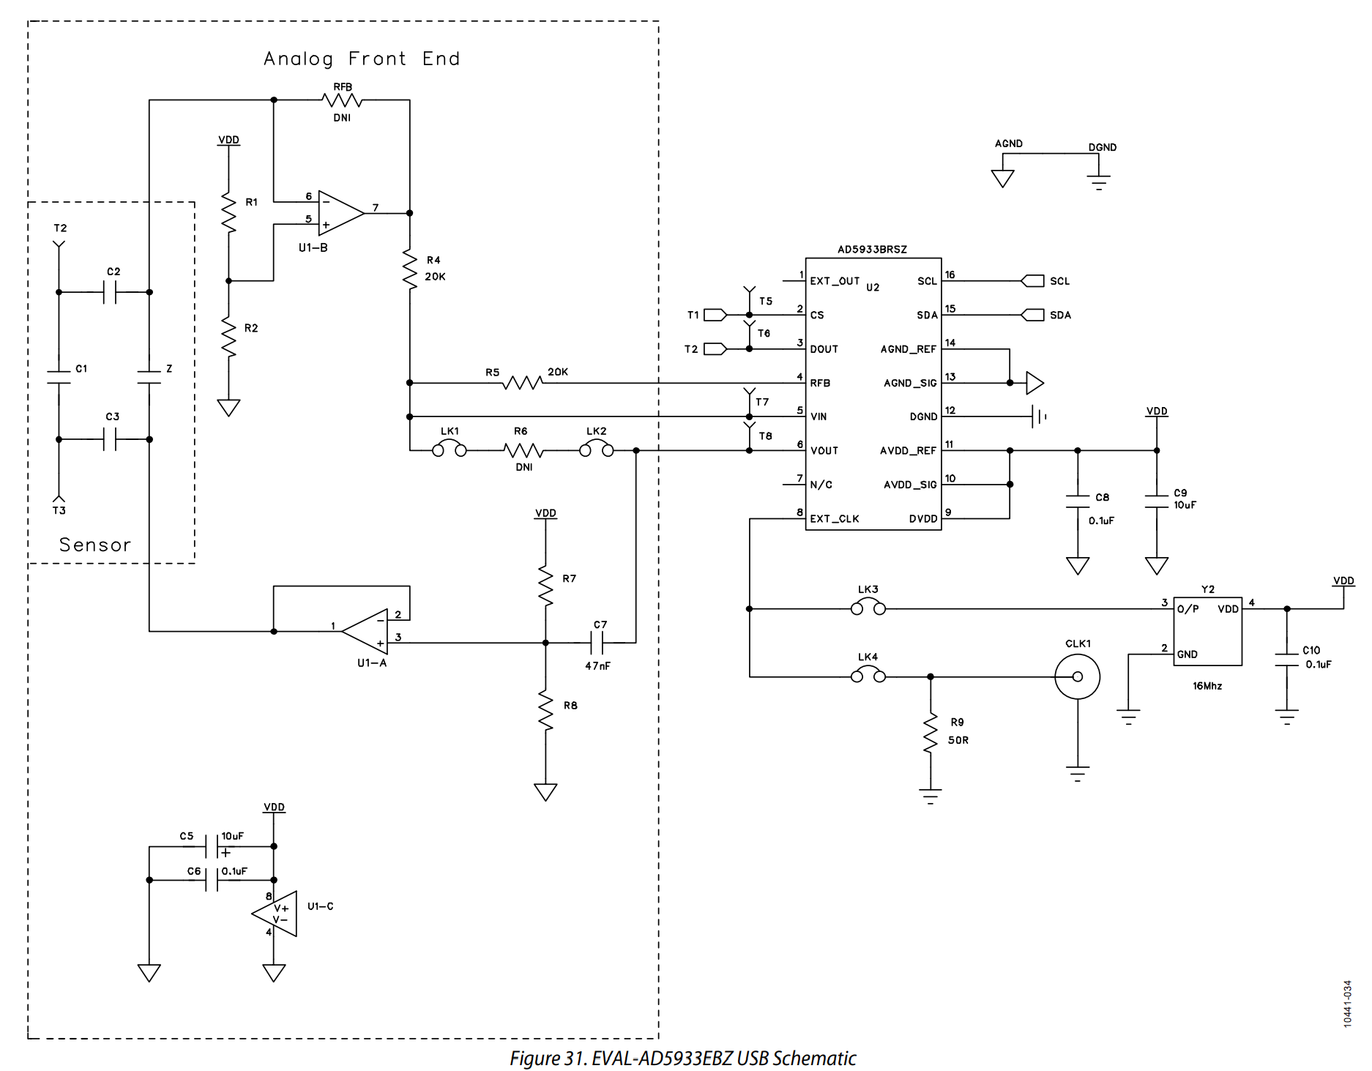
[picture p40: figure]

Senior Design 2022

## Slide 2

Combined Circuit

Determining Body Composition Using Arduino

AD8606


100k

Changed
Resistors

10nF

100k

1M

200k

Same
Voltage Ref
but with Buffer


3.3V

GND

20k

Determining Body Composition Using Arduino

1K

20k

IN A826

Evaluation Board

By cutting jumpers you can enable
Left or Right circuit
You either have one electrode plug on left side
Or you have two on right side

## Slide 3


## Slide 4


If you want LK1 and LK2 controlled digitally you can use analog switch: MC74VHC1GT66
In the example diagram on the right (from an other project),
the capacitor 100nF is connected to ground if SENS_FILTER from
Microcontroller is set high/low.

Needs to be added for callibration


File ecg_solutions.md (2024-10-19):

## ECG Sensor Solutions

### Breakout boards
- [Sparkfun AD8232 Single Lead Heart Rate Monitor, no ADC](https://github.com/sparkfun/AD8232_Heart_Rate_Monitor) $22
- [Protocentral ECG & Respiratory MAX3001](https://protocentral.com/product/protocentral-max30001) $60
- [Protocentral ECG MAX30003](https://protocentral.com/product/protocentral-max30003-single-lead-ecg-breakout-board-v2/) $42
- [Protocentral ECG 3 Channel ADS1293](https://protocentral.com/product/ads1292r-ecg-respiration-breakout-kit/) $48
- [Protocentral ECG & Respiratory ADS1292R](https://protocentral.com/product/ads1292r-ecg-respiration-breakout-kit/) $48

### Analog Front Ends

#### Maxim / Analog Devices
- [MAX30001G](https://www.maximintegrated.com/en/products/analog/data-converters/analog-front-end-ics/MAX30001G.html)
- [MAX30001G Datasheet](https://datasheets.maximintegrated.com/en/ds/MAX30001G.pdf)
- [MAX30003](https://www.maximintegrated.com/en/products/analog/data-converters/analog-front-end-ics/MAX30003.html)
- [MAX30003 Datasheet](https://www.digikey.com/htmldatasheets/production/1994693/0/0/1/max30003.html?utm_adgroup=Integrated%20Circuits&utm_source=google&utm_medium=cpc&utm_campaign=Dynamic%20Search_EN_Product&utm_term=&utm_content=Integrated%20Circuits&gclid=Cj0KCQjwla-hBhD7ARIsAM9tQKvDKbhxIOCwuTKxuGPQEnPMAb2M2XKD20NTcfvLvnXPD3isk3i5nscaAoGZEALw_wcB)

#### Analog Devices
- [General ECG Electrocardiogram (ECG) Measurement Solutions](https://www.analog.com/en/applications/markets/healthcare-pavilion-home/vital-signs-measurement/electrocardiogram-ecg-measurement.html )
- [AD8232, single channel with RL](https://www.analog.com/en/products/ad8232.html)
- [IEEE Paper with AD8232](https://doi.org/10.1109/TIPTEKNO50054.2020.9299248)

#### Texas Instruments
- [General ECG Product and Reference Designs](https://www.ti.com/solution/electrocardiogram-ecg)
- [ADS1293, 3 Channels with RL](https://www.ti.com/general/docs/suppproductinfo.tsp?distId=10&gotoUrl=https%3A%2F%2Fwww.ti.com%2Flit%2Fgpn%2Fads1293)
- [ADS1292R, 2 ECG Channels, 1 Respiration, RL](https://www.ti.com/product/ADS1292R)

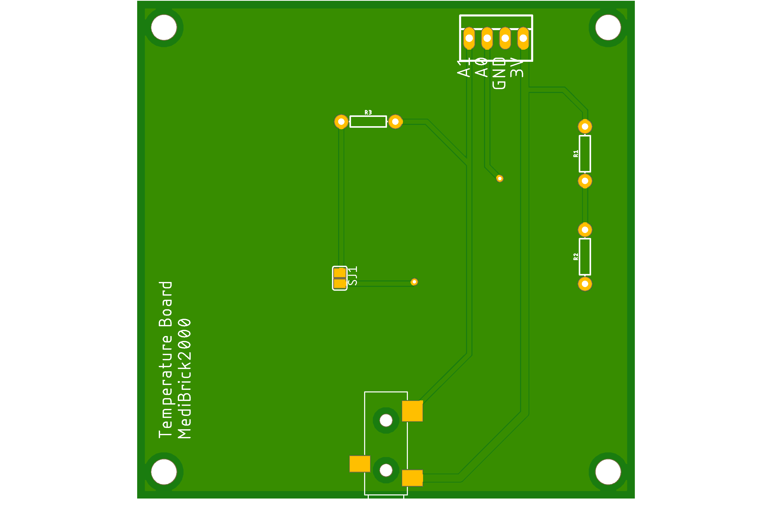
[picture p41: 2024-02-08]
Thermistor_Board/Analog_2024/Feb 3/Temp Schematic.png

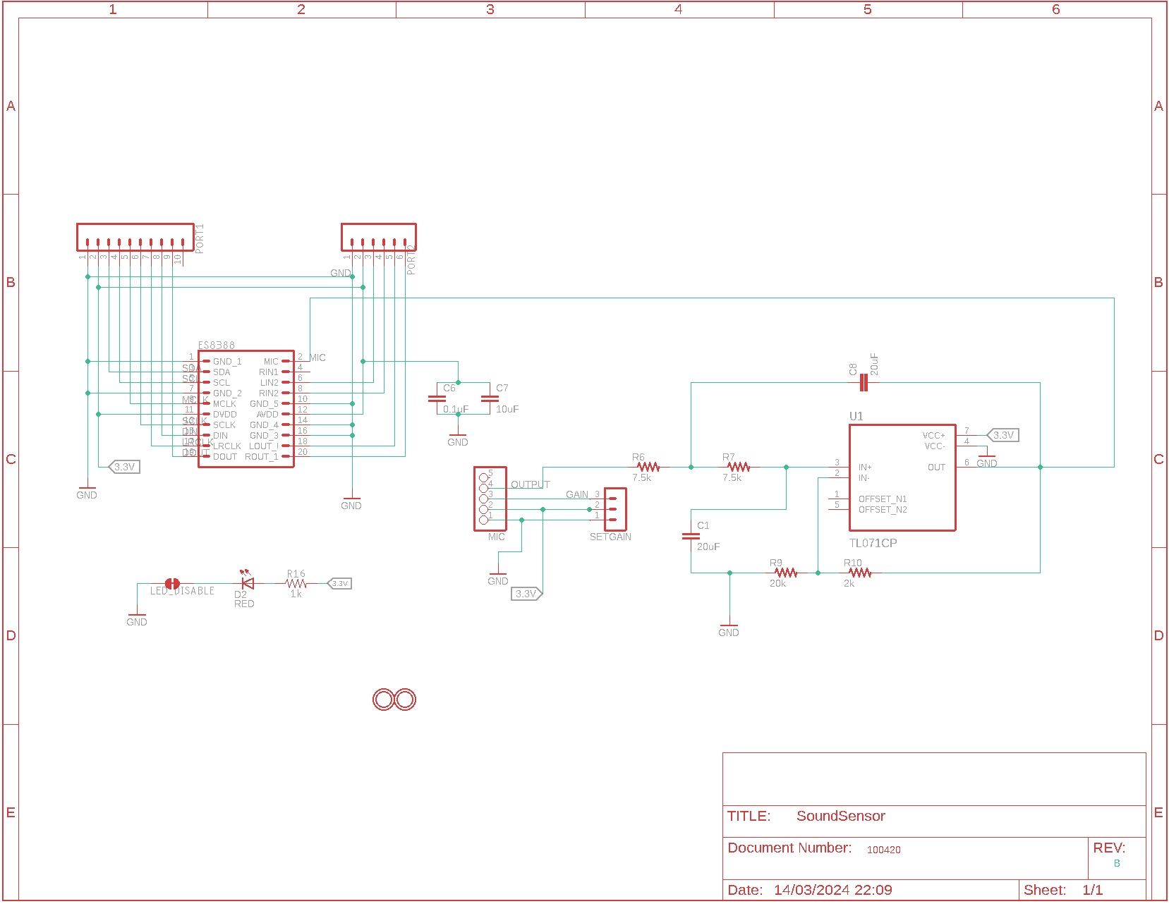
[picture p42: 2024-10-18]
Stethoscope_with_3rdparty_Sound/SoundSensorSchematic.png

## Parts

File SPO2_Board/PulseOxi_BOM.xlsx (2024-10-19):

Item # | Designator | Qty | Manufacturer | Mfg Part # | LCSC Part# | U.S. Distributor | Description / Value | *Package/Footprint | Mounting Type | Your Instructions / Notes
1 | C1,C2,C12,C13,C14 | 5 | Samsung Electro-Mechanics (https://www.lcsc.com/brand-detail/254.html) | CL10A106MA8NRNC (https://www.lcsc.com/product-detail/Multilayer-Ceramic-Capacitors-MLCC-SMD-SMT_Samsung-Electro-Mechanics-CL10A106MA8NRNC_C96446.html) | C96446 (https://www.lcsc.com/product-detail/Multilayer-Ceramic-Capacitors-MLCC-SMD-SMT_Samsung-Electro-Mechanics-CL10A106MA8NRNC_C96446.html) |  | 10uF | 0603 | SMD
2 | C3 | 1 | Samsung Electro-Mechanics (https://www.lcsc.com/brand-detail/254.html) | CL10A105KB8NNNC (https://www.lcsc.com/product-detail/Multilayer-Ceramic-Capacitors-MLCC-SMD-SMT_Samsung-Electro-Mechanics-CL10A105KB8NNNC_C15849.html) | C15849 (https://www.lcsc.com/product-detail/Multilayer-Ceramic-Capacitors-MLCC-SMD-SMT_Samsung-Electro-Mechanics-CL10A105KB8NNNC_C15849.html) |  | 1uF | 0603 | SMD
3 | C4,C7,C8 | 3 | Samsung Electro-Mechanics (https://www.lcsc.com/brand-detail/254.html) | CL10B104KB8NNNC (https://www.lcsc.com/product-detail/Multilayer-Ceramic-Capacitors-MLCC-SMD-SMT_Samsung-Electro-Mechanics-CL10B104KB8NNNC_C1591.html) | C1591 (https://www.lcsc.com/product-detail/Multilayer-Ceramic-Capacitors-MLCC-SMD-SMT_Samsung-Electro-Mechanics-CL10B104KB8NNNC_C1591.html) |  | 0.1uF | 0603 | SMD
4 | C5 | 1 | Samsung Electro-Mechanics (https://www.lcsc.com/brand-detail/254.html) | CL10B103KB8NNNC (https://www.lcsc.com/product-detail/Multilayer-Ceramic-Capacitors-MLCC-SMD-SMT_Samsung-Electro-Mechanics-CL10B103KB8NNNC_C1589.html) | C1589 (https://www.lcsc.com/product-detail/Multilayer-Ceramic-Capacitors-MLCC-SMD-SMT_Samsung-Electro-Mechanics-CL10B103KB8NNNC_C1589.html) |  | 10nF | 0603
5 | C6,C15 | 2 | Samsung Electro-Mechanics (https://www.lcsc.com/brand-detail/254.html) | CL10B222KB8NNNC (https://www.lcsc.com/product-detail/Multilayer-Ceramic-Capacitors-MLCC-SMD-SMT_Samsung-Electro-Mechanics-CL10B222KB8NNNC_C16033.html) | C16033 (https://www.lcsc.com/product-detail/Multilayer-Ceramic-Capacitors-MLCC-SMD-SMT_Samsung-Electro-Mechanics-CL10B222KB8NNNC_C16033.html) |  | 2.2uF | 0603 | SMD
6 | C10,C9 | 2 | Samsung Electro-Mechanics (https://www.lcsc.com/brand-detail/254.html) | CL10C180JB8NNNC (https://www.lcsc.com/product-detail/Multilayer-Ceramic-Capacitors-MLCC-SMD-SMT_Samsung-Electro-Mechanics-CL10C180JB8NNNC_C1647.html) | C1647 (https://www.lcsc.com/product-detail/Multilayer-Ceramic-Capacitors-MLCC-SMD-SMT_Samsung-Electro-Mechanics-CL10C180JB8NNNC_C1647.html) |  | 18pF | 0603 | SMD
7 | C11 | 1 | Samsung Electro-Mechanics (https://www.lcsc.com/brand-detail/254.html) | CL10B104KB8NNNC (https://www.lcsc.com/product-detail/Multilayer-Ceramic-Capacitors-MLCC-SMD-SMT_Samsung-Electro-Mechanics-CL10B104KB8NNNC_C1591.html) | C1591 (https://www.lcsc.com/product-detail/Multilayer-Ceramic-Capacitors-MLCC-SMD-SMT_Samsung-Electro-Mechanics-CL10B104KB8NNNC_C1591.html) |  | 100nF | 0603 | SMD
8 | D1 | 1 | XINGLIGHT | XL-1608UBC-04 (https://www.lcsc.com/product-detail/Light-Emitting-Diodes-LED_XINGLIGHT-XL-1608UBC-04_C965807.html) | C965807 (https://www.lcsc.com/product-detail/Light-Emitting-Diodes-LED_XINGLIGHT-XL-1608UBC-04_C965807.html) |  | BLUE LED | 0603 | SMD
9 | D4,D6,D7,D8 | 4 | Diodes Incorporated | BAV99W-7-F | C93035 (https://www.lcsc.com/product-detail/Switching-Diode_Diodes-Incorporated-BAV99W-7-F_C93035.html) |  | Schottky Barrier Diodes | SOT-323 | SMD
10 | IC1 | 1 | Texas Instruments (https://www.lcsc.com/brand-detail/100.html) | AFE4490RHAR | C2651608 (https://www.lcsc.com/product-detail/Analog-Front-End-AFEs_Texas-Instruments-AFE4490RHAR_C2651608.html) | https://www.mouser.com/ProductDetail/Texas-Instruments/AFE4490RHAR?qs=%2FrNExBQRqEStAPdZrnasYQ%3D%3D | Analog Front End (AFEs) | VQFN-40 | SMD
11 | L1,L2,L3,L4 | 4 | Taiyo Yuden | LBC3225T100KR | C223424 (https://www.lcsc.com/product-detail/Power-Inductors_Taiyo-Yuden-LBC3225T100KR_C223424.html) |  | INDUCTOR 10uH | 1210 | SMD
12 | R1,R16 | 2 | YAGEO (https://www.lcsc.com/brand-detail/396.html) | RC0603FR-071KL (https://www.lcsc.com/product-detail/Chip-Resistor-Surface-Mount_YAGEO-RC0603FR-071KL_C22548.html) | C22548 (https://www.lcsc.com/product-detail/Chip-Resistor-Surface-Mount_YAGEO-RC0603FR-071KL_C22548.html) |  | 1K | 0603 | SMD
13 | R2,R3,R5,R6,R7,R8,R9,R10,R11,R12,R13 | 11 | YAGEO (https://www.lcsc.com/brand-detail/396.html) | AC0603FR-0710RL (https://www.lcsc.com/product-detail/Chip-Resistor-Surface-Mount_YAGEO-AC0603FR-0710RL_C138286.html) | C138286 (https://www.lcsc.com/product-detail/Chip-Resistor-Surface-Mount_YAGEO-AC0603FR-0710RL_C138286.html) |  | 10 | 0603 | SMD
14 | R4 | 1 | YAGEO (https://www.lcsc.com/brand-detail/396.html) | RC0603FR-0710KL (https://www.lcsc.com/product-detail/Chip-Resistor-Surface-Mount_YAGEO-RC0603FR-0710KL_C98220.html) | C98220 (https://www.lcsc.com/product-detail/Chip-Resistor-Surface-Mount_YAGEO-RC0603FR-0710KL_C98220.html) |  | 10K | 0603
15 | OSC | 1 | Abracon LLC (https://www.lcsc.com/brand-detail/1136.html) | ABM3-8.000MHZ-D2Y-T (https://www.lcsc.com/product-detail/Crystals_Abracon-LLC-ABM3-8-000MHZ-D2Y-T_C144380.html) | C144380 (https://www.lcsc.com/product-detail/Crystals_Abracon-LLC-ABM3-8-000MHZ-D2Y-T_C144380.html) |  | Oscillator, 8MHz | 5032 | SMD
16 | X2 | 1 | TE Connectivity | 2301843-1 (https://www.lcsc.com/product-detail/D-Sub-VGA-connector_TE-Connectivity-2301843-1_C3118153.html) | C3118153 (https://www.lcsc.com/product-detail/D-Sub-VGA-connector_TE-Connectivity-2301843-1_C3118153.html) |  | DB9 CONNECTOR | Tray | Throughole

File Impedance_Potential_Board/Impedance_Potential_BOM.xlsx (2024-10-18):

Item # | Designator | Qty | Manufacturer | Mfg Part # | LCSC Part# | U.S. Distributor | Description / Value | Packaging | Type | Cost
1 | C1, C2 | 2 | Samsung Electro-Mechanics (https://www.lcsc.com/brand-detail/254.html) | CL10B224KA8NNNC (https://www.lcsc.com/product-detail/Multilayer-Ceramic-Capacitors-MLCC-SMD-SMT_Samsung-Electro-Mechanics-CL10B224KA8NNNC_C21120.html) | C21120 (https://www.lcsc.com/product-detail/Multilayer-Ceramic-Capacitors-MLCC-SMD-SMT_Samsung-Electro-Mechanics-CL10B224KA8NNNC_C21120.html) |  | 0.22uF Ceramic Capacitor >=25V | 603 | SMD | 0.0052
2 | C3, C4, C6, C7 | 4 | Samsung Electro-Mechanics (https://www.lcsc.com/brand-detail/254.html) | CL10C100JB8NNNC (https://www.lcsc.com/product-detail/Multilayer-Ceramic-Capacitors-MLCC-SMD-SMT_Samsung-Electro-Mechanics-CL10C100JB8NNNC_C1634.html) | C1634 (https://www.lcsc.com/product-detail/Multilayer-Ceramic-Capacitors-MLCC-SMD-SMT_Samsung-Electro-Mechanics-CL10C100JB8NNNC_C1634.html) |  | 10pF Ceramic Capacitor >=25V | 603 | SMD | 0.0053
3 | C5 | 1 | Samsung Electro-Mechanics (https://www.lcsc.com/brand-detail/254.html) | CL10C470JB8NNNC (https://www.lcsc.com/product-detail/Multilayer-Ceramic-Capacitors-MLCC-SMD-SMT_Samsung-Electro-Mechanics-CL10C470JB8NNNC_C1671.html) | C1671 (https://www.lcsc.com/product-detail/Multilayer-Ceramic-Capacitors-MLCC-SMD-SMT_Samsung-Electro-Mechanics-CL10C470JB8NNNC_C1671.html) |  | 47pF Ceramic Capacitor >=25V | 603 | SMD | 0.006
4 | C8 | 1 | Samsung Electro-Mechanics (https://www.lcsc.com/brand-detail/254.html) | CL10B222KB8NNNC (https://www.lcsc.com/product-detail/Multilayer-Ceramic-Capacitors-MLCC-SMD-SMT_Samsung-Electro-Mechanics-CL10B222KB8NNNC_C16033.html) | C16033 (https://www.lcsc.com/product-detail/Multilayer-Ceramic-Capacitors-MLCC-SMD-SMT_Samsung-Electro-Mechanics-CL10B222KB8NNNC_C16033.html) |  | 2.2nF Ceramic Capacitor >=25V | 603 | SMD | 0.0057
5 | C9, C12, C14, C19, C20, C21 | 6 | Samsung Electro-Mechanics (https://www.lcsc.com/brand-detail/254.html) | CL10A106MA8NRNC (https://www.lcsc.com/product-detail/Multilayer-Ceramic-Capacitors-MLCC-SMD-SMT_Samsung-Electro-Mechanics-CL10A106MA8NRNC_C96446.html) | C96446 (https://www.lcsc.com/product-detail/Multilayer-Ceramic-Capacitors-MLCC-SMD-SMT_Samsung-Electro-Mechanics-CL10A106MA8NRNC_C96446.html) |  | 10uF Ceramic Capacitor >=25V | 603 | SMD | 0.0169
6 | C10, C15, C16 | 3 | Samsung Electro-Mechanics (https://www.lcsc.com/brand-detail/254.html) | CL10A105KB8NNNC (https://www.lcsc.com/product-detail/Multilayer-Ceramic-Capacitors-MLCC-SMD-SMT_Samsung-Electro-Mechanics-CL10A105KB8NNNC_C15849.html) | C15849 (https://www.lcsc.com/product-detail/Multilayer-Ceramic-Capacitors-MLCC-SMD-SMT_Samsung-Electro-Mechanics-CL10A105KB8NNNC_C15849.html) |  | 1.0uF Ceramic | 603 | SMD | 0.0042
7 | C11, C13, C17 | 3 | Samsung Electro-Mechanics (https://www.lcsc.com/brand-detail/254.html) | CL10B104KB8NNNC (https://www.lcsc.com/product-detail/Multilayer-Ceramic-Capacitors-MLCC-SMD-SMT_Samsung-Electro-Mechanics-CL10B104KB8NNNC_C1591.html) | C1591 (https://www.lcsc.com/product-detail/Multilayer-Ceramic-Capacitors-MLCC-SMD-SMT_Samsung-Electro-Mechanics-CL10B104KB8NNNC_C1591.html) |  | 0.1uF Ceramic Capacitor >=25V | 603 | SMD | 0.0024
8 | C18 | 1 | Samsung Electro-Mechanics (https://www.lcsc.com/brand-detail/254.html) | CL10B102KB8NNNC (https://www.lcsc.com/product-detail/Multilayer-Ceramic-Capacitors-MLCC-SMD-SMT_Samsung-Electro-Mechanics-CL10B102KB8NNNC_C1588.html) | C1588 (https://www.lcsc.com/product-detail/Multilayer-Ceramic-Capacitors-MLCC-SMD-SMT_Samsung-Electro-Mechanics-CL10B102KB8NNNC_C1588.html) |  | 1nF Ceramic Capacitor >= 25V | 603 | SMD | 0.0027
9 | C22, C23 | 2 | Samsung Electro-Mechanics (https://www.lcsc.com/brand-detail/254.html) | CL10B473KB8NNNC (https://www.lcsc.com/product-detail/Multilayer-Ceramic-Capacitors-MLCC-SMD-SMT_Samsung-Electro-Mechanics-CL10B473KB8NNNC_C1622.html) | C1622 (https://www.lcsc.com/product-detail/Multilayer-Ceramic-Capacitors-MLCC-SMD-SMT_Samsung-Electro-Mechanics-CL10B473KB8NNNC_C1622.html) |  | 47nF Ceramic Capacitor >=25V | 603 | SMD | 0.0043
10 | R1, R2 | 2 | YAGEO (https://www.lcsc.com/brand-detail/396.html) | RC0603FR-0751KL (https://www.lcsc.com/product-detail/Chip-Resistor-Surface-Mount_YAGEO-RC0603FR-0751KL_C107231.html) | C107231 (https://www.lcsc.com/product-detail/Chip-Resistor-Surface-Mount_YAGEO-RC0603FR-0751KL_C107231.html) |  | 51k 100mW Resistor | 603 | SMD | 0.0012
11 | R4 | 1 | YAGEO (https://www.lcsc.com/brand-detail/396.html) | RT0603BRE07324KL (https://www.lcsc.com/product-detail/Chip-Resistor-Surface-Mount_YAGEO-RT0603BRE07324KL_C861836.html) | C861836 (https://www.lcsc.com/product-detail/Chip-Resistor-Surface-Mount_YAGEO-RT0603BRE07324KL_C861836.html) |  | 324k 100mW Resistor | 603 | SMD | 0.019
12 | R5, R6, R7, R8, R9, R10 | 6 | YAGEO (https://www.lcsc.com/brand-detail/396.html) | RC0603JR-0710RL (https://www.lcsc.com/product-detail/Chip-Resistor-Surface-Mount_YAGEO-RC0603JR-0710RL_C109317.html) | C109317 (https://www.lcsc.com/product-detail/Chip-Resistor-Surface-Mount_YAGEO-RC0603JR-0710RL_C109317.html) |  | 10 100mW Resistor | 603 | SMD | 0.0019
13 | R11, R12, R13, R14, R15, R17 | 6 | YAGEO (https://www.lcsc.com/brand-detail/396.html) | RC0603FR-07100KL (https://www.lcsc.com/product-detail/Chip-Resistor-Surface-Mount_YAGEO-RC0603FR-07100KL_C14675.html) | C14675 (https://www.lcsc.com/product-detail/Chip-Resistor-Surface-Mount_YAGEO-RC0603FR-07100KL_C14675.html) |  | 100k 100mW Resistor | 603 | SMD | 0.0009
14 | R16 | 1 | YAGEO (https://www.lcsc.com/brand-detail/396.html) | RC0603FR-071KL (https://www.lcsc.com/product-detail/Chip-Resistor-Surface-Mount_YAGEO-RC0603FR-071KL_C22548.html) | C22548 (https://www.lcsc.com/product-detail/Chip-Resistor-Surface-Mount_YAGEO-RC0603FR-071KL_C22548.html) |  | 1k 100mW Resistor | 603 | SMD | 0.0009
15 | R18 | 1 | YAGEO (https://www.lcsc.com/brand-detail/396.html) | RC0603JR-07100RL (https://www.lcsc.com/product-detail/Chip-Resistor-Surface-Mount_YAGEO-RC0603JR-07100RL_C110091.html) | C110091 (https://www.lcsc.com/product-detail/Chip-Resistor-Surface-Mount_YAGEO-RC0603JR-07100RL_C110091.html) |  | 100 100mW Resistor | 603 | SMD | 0.0011
16 | R19, R20, R21, R22 | 4 | YAGEO (https://www.lcsc.com/brand-detail/396.html) | RC0603JR-070RL (https://www.lcsc.com/product-detail/Chip-Resistor-Surface-Mount_YAGEO-RC0603JR-070RL_C95177.html) | C95177 (https://www.lcsc.com/product-detail/Chip-Resistor-Surface-Mount_YAGEO-RC0603JR-070RL_C95177.html) |  | 0 100mW Resistor | 603 | SMD | 0.001
17 | R23 | 1 | YAGEO (https://www.lcsc.com/brand-detail/396.html) | RT0603BRD07200KL | C728585 (https://www.lcsc.com/product-detail/Chip-Resistor-Surface-Mount_YAGEO-RT0603BRD07200KL_C728585.html) |  | 200k Resistor | 603 | SMD | 0.023
18 | D2, D3, D4, D5, D6, D7, D8 | 7 | onsemi (https://www.lcsc.com/brand-detail/94.html) | ESD7551N2T5G (https://www.lcsc.com/product-detail/Electrostatic-and-Surge-Protection-TVS-span-style-background-color-ff0-ESD-span_Leiditech-ESD7551N2T5G_C5123457.html) | C5123457 (https://www.lcsc.com/product-detail/Electrostatic-and-Surge-Protection-TVS-span-style-background-color-ff0-ESD-span_Leiditech-ESD7551N2T5G_C5123457.html) | https://www.mouser.com/ProductDetail/onsemi/ESD7551N2T5G?qs=5aG0NVq1C4x8NutXGbtG6w%3D%3D | ESD7551N2T5G, Protection Diode | ESD7551N2T5G | SMD | 0.0932
19 | D1 | 1 | XINGLIGHT | XL-1608UBC-04 (https://www.lcsc.com/product-detail/Light-Emitting-Diodes-LED_XINGLIGHT-XL-1608UBC-04_C965807.html) | C965807 (https://www.lcsc.com/product-detail/Light-Emitting-Diodes-LED_XINGLIGHT-XL-1608UBC-04_C965807.html) |  | Blue LED | 603 | SMD | 0.0034
20 | IC1 | 1 | Analog Devices/Maxim | MAX30001GCWV+ |  | https://www.mouser.com/ProductDetail/Analog-Devices-Maxim-Integrated/MAX30001GCWV%2b?qs=Rp5uXu7WBW%2FLfomdQH9F5g%3D%3D | MAX30001GCWV+ | BGA30C50P6X5_293X274X69 | SMD | 10.44
21 | U4 | 1 | Diodes Incorporated (https://www.lcsc.com/brand-detail/296.html) | AP2112K-1.8TRG1 (https://www.lcsc.com/product-detail/Linear-Voltage-Regulators-LDO_Diodes-Incorporated-AP2112K-1-8TRG1_C176944.html) | C176944 (https://www.lcsc.com/product-detail/Linear-Voltage-Regulators-LDO_Diodes-Incorporated-AP2112K-1-8TRG1_C176944.html) | https://www.mouser.com/ProductDetail/Diodes-Incorporated/AP2112K-1.8TRG1?qs=x6A8l6qLYDBx1xhw8AX2cw%3D%3D | AP2112K-1.8V V_REG_LDO SMD | SOT-25 | SMD
22 | DRV, ECG, IMPEDANCE | 3 | CUI Devices (https://www.lcsc.com/brand-detail/15740.html) | SJ-3523-SMT-TR (https://www.lcsc.com/product-detail/Audio-Connectors_CUI-Devices-SJ-3523-SMT-TR_C4991872.html) | C4991872 | https://www.mouser.com/ProductDetail/CUI-Devices/SJ-3523-SMT-TR?qs=WyjlAZoYn51zOHzJ3r4ZRA%3D%3D | 3.5mm Audio Jack, Low Profils, Stereo 3 pin Right Angle | CUI_SJ-3523-SMT-TR | SMD | 1.01

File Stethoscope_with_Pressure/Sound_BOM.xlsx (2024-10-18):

Item # | Designator | Qty | Manufacturer | Mfg Part # | LCSC Part# | U.S. Distributor | Description / Value | *Package/Footprint | Mounting Type | Your Instructions / Notes
1 | C2, C7, C9, C10, C11, C12, C13, C28 | 8 | Samsung Electro-Mechanics (https://www.lcsc.com/brand-detail/254.html) | CL10B104KA8NNNC (https://www.lcsc.com/product-detail/Multilayer-Ceramic-Capacitors-MLCC-SMD-SMT_Samsung-Electro-Mechanics-CL10B104KA8NNNC_C1590.html) | C1590 (https://www.lcsc.com/product-detail/Multilayer-Ceramic-Capacitors-MLCC-SMD-SMT_Samsung-Electro-Mechanics-CL10B104KA8NNNC_C1590.html) |  | 0.1uF | 0603 | SMD
2 | C4, C21, C22, C23, C24, C27 | 6 | Samsung Electro-Mechanics (https://www.lcsc.com/brand-detail/254.html) | CL10A105KA8NNNC (https://www.lcsc.com/product-detail/Multilayer-Ceramic-Capacitors-MLCC-SMD-SMT_Samsung-Electro-Mechanics-CL10A105KA8NNNC_C5673.html) | C5673 (https://www.lcsc.com/product-detail/Multilayer-Ceramic-Capacitors-MLCC-SMD-SMT_Samsung-Electro-Mechanics-CL10A105KA8NNNC_C5673.html) |  | 1.0uF | 0603 | SMD
3 | C3, C15, C16, C17, C18, C19, C20, C29 | 8 | Samsung Electro-Mechanics (https://www.lcsc.com/brand-detail/254.html) | CL10A106MA8NRNC (https://www.lcsc.com/product-detail/Multilayer-Ceramic-Capacitors-MLCC-SMD-SMT_Samsung-Electro-Mechanics-CL10A106MA8NRNC_C96446.html) | C96446 (https://www.lcsc.com/product-detail/Multilayer-Ceramic-Capacitors-MLCC-SMD-SMT_Samsung-Electro-Mechanics-CL10A106MA8NRNC_C96446.html) |  | 10uF | 0603 | SMD
4 | C1, C6 | 2 | Samsung Electro-Mechanics (https://www.lcsc.com/brand-detail/254.html) | CL10A475KA8NQNC (https://www.lcsc.com/product-detail/Multilayer-Ceramic-Capacitors-MLCC-SMD-SMT_Samsung-Electro-Mechanics-CL10A475KA8NQNC_C69335.html) | C69335 (https://www.lcsc.com/product-detail/Multilayer-Ceramic-Capacitors-MLCC-SMD-SMT_Samsung-Electro-Mechanics-CL10A475KA8NQNC_C69335.html) |  | 4.7uF | 0603 | SMD
5 | C5, C8 | 2 | Samsung Electro-Mechanics (https://www.lcsc.com/brand-detail/254.html) | CL10C102JB8NNNC (https://www.lcsc.com/product-detail/Multilayer-Ceramic-Capacitors-MLCC-SMD-SMT_Samsung-Electro-Mechanics-CL10C102JB8NNNC_C163508.html) | C163508 (https://www.lcsc.com/product-detail/Multilayer-Ceramic-Capacitors-MLCC-SMD-SMT_Samsung-Electro-Mechanics-CL10C102JB8NNNC_C163508.html) |  | 1000pF | 0603 | SMD | Was 82.pF in version 2
6 | C25, C26 | 2 | Samsung Electro-Mechanics (https://www.lcsc.com/brand-detail/254.html) | CL10A476MQ8QRNC (https://www.lcsc.com/product-detail/Multilayer-Ceramic-Capacitors-MLCC-SMD-SMT_Samsung-Electro-Mechanics-CL10A476MQ8QRNC_C730416.html) | C730416 (https://www.lcsc.com/product-detail/Multilayer-Ceramic-Capacitors-MLCC-SMD-SMT_Samsung-Electro-Mechanics-CL10A476MQ8QRNC_C730416.html) |  | 47uF | 0603 | SMD
7 | C30 | 1 | Samsung Electro-Mechanics (https://www.lcsc.com/brand-detail/254.html) | CL10B102KB8NNNC (https://www.lcsc.com/product-detail/Multilayer-Ceramic-Capacitors-MLCC-SMD-SMT_Samsung-Electro-Mechanics-CL10B102KB8NNNC_C1588.html) | C1588 (https://www.lcsc.com/product-detail/Multilayer-Ceramic-Capacitors-MLCC-SMD-SMT_Samsung-Electro-Mechanics-CL10B102KB8NNNC_C1588.html) |  | 1nF | 0603 | SMD
8 | C31, C32 | 2 | Samsung Electro-Mechanics (https://www.lcsc.com/brand-detail/254.html) | CL10C220JB8NNNC (https://www.lcsc.com/product-detail/Multilayer-Ceramic-Capacitors-MLCC-SMD-SMT_Samsung-Electro-Mechanics-CL10C220JB8NNNC_C1653.html) | C1653 (https://www.lcsc.com/product-detail/Multilayer-Ceramic-Capacitors-MLCC-SMD-SMT_Samsung-Electro-Mechanics-CL10C220JB8NNNC_C1653.html) |  | 22pF | 0603 | SMD
9 | R1, R5 | 2 | YAGEO (https://www.lcsc.com/brand-detail/396.html) | RC0603FR-074K7L (https://www.lcsc.com/product-detail/Chip-Resistor-Surface-Mount_YAGEO-RC0603FR-074K7L_C99782.html) | C99782 (https://www.lcsc.com/product-detail/Chip-Resistor-Surface-Mount_YAGEO-RC0603FR-074K7L_C99782.html) |  | 4.7k | 0603 | SMD
10 | R2, R3, R12, R15, R17 | 5 | YAGEO (https://www.lcsc.com/brand-detail/396.html) | RC0603FR-0710KL (https://www.lcsc.com/product-detail/Chip-Resistor-Surface-Mount_YAGEO-RC0603FR-0710KL_C98220.html) | C98220 (https://www.lcsc.com/product-detail/Chip-Resistor-Surface-Mount_YAGEO-RC0603FR-0710KL_C98220.html) |  | 10k | 0603 | SMD
11 | R4, R8 | 2 | YAGEO (https://www.lcsc.com/brand-detail/396.html) | RC0603FR-078K2L (https://www.lcsc.com/product-detail/Chip-Resistor-Surface-Mount_YAGEO-RC0603FR-078K2L_C114637.html) | C114637 (https://www.lcsc.com/product-detail/Chip-Resistor-Surface-Mount_YAGEO-RC0603FR-078K2L_C114637.html) |  | 8.2k | 0603 | SMD | Was 100k in version 2
12 | R6, R7, R9, R10, R11 | 5 | YAGEO (https://www.lcsc.com/brand-detail/396.html) | RC0603FR-0733RL (https://www.lcsc.com/product-detail/Chip-Resistor-Surface-Mount_YAGEO-RC0603FR-0733RL_C108661.html) | C108661 (https://www.lcsc.com/product-detail/Chip-Resistor-Surface-Mount_YAGEO-RC0603FR-0733RL_C108661.html) |  | 33 | 0603 | SMD
13 | R13, R14 | 2 | YAGEO (https://www.lcsc.com/brand-detail/396.html) | RC0603FR-072KL (https://www.lcsc.com/product-detail/Chip-Resistor-Surface-Mount_YAGEO-RC0603FR-072KL_C105576.html) | C105576 (https://www.lcsc.com/product-detail/Chip-Resistor-Surface-Mount_YAGEO-RC0603FR-072KL_C105576.html) |  | 2k | 0603 | SMD
14 | R16 | 1 | YAGEO (https://www.lcsc.com/brand-detail/396.html) | RC0603FR-071KL (https://www.lcsc.com/product-detail/Chip-Resistor-Surface-Mount_YAGEO-RC0603FR-071KL_C22548.html) | C22548 (https://www.lcsc.com/product-detail/Chip-Resistor-Surface-Mount_YAGEO-RC0603FR-071KL_C22548.html) |  | 1k | 0603 | SMD
15 | R18, R19, R20 | 3 | YAGEO (https://www.lcsc.com/brand-detail/396.html) | RC0603FR-07100RL (https://www.lcsc.com/product-detail/Chip-Resistor-Surface-Mount_YAGEO-RC0603FR-07100RL_C105588.html) | C105588 (https://www.lcsc.com/product-detail/Chip-Resistor-Surface-Mount_YAGEO-RC0603FR-07100RL_C105588.html) |  | 100 | 0603 | SMD
16 | R21 | 1 | YAGEO (https://www.lcsc.com/brand-detail/396.html) | RC0603FR-074R7L (https://www.lcsc.com/product-detail/Chip-Resistor-Surface-Mount_YAGEO-RC0603FR-074R7L_C137705.html) | C137705 (https://www.lcsc.com/product-detail/Chip-Resistor-Surface-Mount_YAGEO-RC0603FR-074R7L_C137705.html) |  | 4.7 | 0603 | SMD
17 | R22 | 1 | YAGEO (https://www.lcsc.com/brand-detail/396.html) | RC0603FR-073K3L (https://www.lcsc.com/product-detail/Chip-Resistor-Surface-Mount_YAGEO-RC0603FR-073K3L_C108078.html) | C108078 (https://www.lcsc.com/product-detail/Chip-Resistor-Surface-Mount_YAGEO-RC0603FR-073K3L_C108078.html) |  | 3.3k | 0603 | SMD
18 | LS1, LS2 | 2 | PUI Audio, Inc. (https://www.lcsc.com/brand-detail/13209.html) | AMM-2742-T-R (https://www.lcsc.com/product-detail/MEMS-Microphones_PUI-Audio-Inc-AMM-2742-T-R_C3171735.html) | C3171735 (https://www.lcsc.com/product-detail/MEMS-Microphones_PUI-Audio-Inc-AMM-2742-T-R_C3171735.html) | https://www.mouser.com/ProductDetail/PUI-Audio/AMM-2742-T-R?qs=zhx2xqPtQQyJoGop0O%252BpMA%3D%3D | AMM-2742-T-R, MEMS Microphones | 0603 | SMD
19 | IC1 | 1 | Everest-semi(Everest Semiconductor) (https://www.lcsc.com/brand-detail/11902.html) | ES8388 (https://www.lcsc.com/product-detail/ADCs-DACs-Special-Purpose_Everest-semi-Everest-Semiconductor-ES8388_C365736.html) | C365736 (https://www.lcsc.com/product-detail/ADCs-DACs-Special-Purpose_Everest-semi-Everest-Semiconductor-ES8388_C365736.html) |  | ES8388 | QFN-28-EP(4x4) | SMD
20 | D1 | 1 | XINGLIGHT | XL-1608UBC-04 (https://www.lcsc.com/product-detail/Light-Emitting-Diodes-LED_XINGLIGHT-XL-1608UBC-04_C965807.html) | C965807 (https://www.lcsc.com/product-detail/Light-Emitting-Diodes-LED_XINGLIGHT-XL-1608UBC-04_C965807.html) |  | Blue LED | 0603 | SMD
21 | J1 | 1 | CUI Devices (https://www.lcsc.com/brand-detail/15740.html) | SJ-3523-SMT-TR (https://www.lcsc.com/product-detail/Audio-Connector-Headphone_CUI-Devices-SJ-3523-SMT-TR_C4991872.html) |  | https://www.mouser.com/ProductDetail/CUI-Devices/SJ-3523-SMT-TR?qs=WyjlAZoYn51zOHzJ3r4ZRA%3D%3D | SJ-3523-SMT-TR, 3.5mm Audio Jack |  | SMD
22 | J3 | 1 | CUI Devices (https://www.lcsc.com/brand-detail/15740.html) | SJ2-3574A-SMT-TR (https://www.lcsc.com/product-detail/Audio-Connector-Headphone_CUI-Devices-SJ2-3574A-SMT-TR_C4991637.html) |  | https://www.mouser.com/ProductDetail/CUI-Devices/SJ2-3574A-SMT-TR?qs=DXv0QSHKF4zeQKpjIMxQnA%3D%3D | SJ2-3574A-SMT-TR, 3.5mm Audio Jack with microphone |  | SMD
23 | IC2 | 1 | Texas Instruments (https://www.lcsc.com/brand-detail/100.html) | TLV9002IDDFR (https://www.lcsc.com/product-detail/Operational-Amplifier_Texas-Instruments-TLV9002IDDFR_C2862620.html) | C2862620 (https://www.lcsc.com/product-detail/Operational-Amplifier_Texas-Instruments-TLV9002IDDFR_C2862620.html) |  | TLV9002IDDFR, Dual OpAmp | TSOT-23-8 | SMD
 |  | 60
 | Resistors | 22
 | Capacitors | 31

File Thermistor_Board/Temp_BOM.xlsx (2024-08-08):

Item | *Designator | *Qty | Manufacturer | *Mfg Part # | Description / Value | *Package/Footprint | LCSC Part # | U.S. Distributor
1 | C2 | 1 | Samsung Electro-Mechanics (https://www.lcsc.com/brand-detail/254.html) | CL10B104KB8NNNC (https://www.lcsc.com/product-detail/Multilayer-Ceramic-Capacitors-MLCC-SMD-SMT_Samsung-Electro-Mechanics-CL10B104KB8NNNC_C1591.html) | 0.1uF | 603 | C1591 (https://www.lcsc.com/product-detail/Multilayer-Ceramic-Capacitors-MLCC-SMD-SMT_Samsung-Electro-Mechanics-CL10B104KB8NNNC_C1591.html)
2 | R1, R5, R8 | 9 | YAGEO (https://www.lcsc.com/brand-detail/396.html) | RC0603FR-0710KL (https://www.lcsc.com/product-detail/Chip-Resistor-Surface-Mount_YAGEO-RC0603FR-0710KL_C98220.html) | 10k | 603 | C98220 (https://www.lcsc.com/product-detail/Chip-Resistor-Surface-Mount_YAGEO-RC0603FR-0710KL_C98220.html)
3 | R2, R3, R4, R6, R9, R7 |  | YAGEO (https://www.lcsc.com/brand-detail/396.html) | RC0402FR-07100KL (https://www.lcsc.com/product-detail/Chip-Resistor-Surface-Mount_YAGEO-RC0402FR-07100KL_C60491.html) | 20k | 603 | C60491 (https://www.lcsc.com/product-detail/Chip-Resistor-Surface-Mount_YAGEO-RC0402FR-07100KL_C60491.html)
4 | C1 | 1 | Samsung Electro-Mechanics (https://www.lcsc.com/brand-detail/254.html) | CL10A106MA8NRNC (https://www.lcsc.com/product-detail/Multilayer-Ceramic-Capacitors-MLCC-SMD-SMT_Samsung-Electro-Mechanics-CL10A106MA8NRNC_C96446.html) | 10uF | 603 | C96446 (https://www.lcsc.com/product-detail/Multilayer-Ceramic-Capacitors-MLCC-SMD-SMT_Samsung-Electro-Mechanics-CL10A106MA8NRNC_C96446.html)
5 | R16 | 1 | YAGEO (https://www.lcsc.com/brand-detail/396.html) | RC0603FR-071KL (https://www.lcsc.com/product-detail/Chip-Resistor-Surface-Mount_YAGEO-RC0603FR-071KL_C22548.html) | 1k | 603 | C22548 (https://www.lcsc.com/product-detail/Chip-Resistor-Surface-Mount_YAGEO-RC0603FR-071KL_C22548.html)
6 | D1 | 1 | XINGLIGHT | XL-1608UBC-04 (https://www.lcsc.com/product-detail/Light-Emitting-Diodes-LED_XINGLIGHT-XL-1608UBC-04_C965807.html) | Blue LED | 603 | C965807 (https://www.lcsc.com/product-detail/Light-Emitting-Diodes-LED_XINGLIGHT-XL-1608UBC-04_C965807.html)
7 | J2, J3, J5 | 3 | CUI Devices (https://www.lcsc.com/brand-detail/15740.html) | SJ-3523-SMT-TR (https://www.lcsc.com/product-detail/Audio-Connectors_CUI-Devices-SJ-3523-SMT-TR_C4991872.html) | Audio Jack Connector 3.5 mm Low Profile Surface Mount Stereo Jack, 3 Pin Right-Angle Check availability | CUI_SJ-3523-SMT-TR | C4991872 | https://www.mouser.com/ProductDetail/CUI-Devices/SJ-3523-SMT-TR?qs=WyjlAZoYn51zOHzJ3r4ZRA%3D%3D
 |  | 16

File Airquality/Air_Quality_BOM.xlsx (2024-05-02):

Item # | Designator | Quantity | Manufacturer | Mfg Part # | Description / Value | Package/Footprint | Part # LCSC | U.S. Distributor | Cost | Cost 10 | Cost 100
1 | I2C_IN, I2C_OUT | 2 | BOOMELE(Boom Precision Elec) | 1.0T-4P (https://www.lcsc.com/product-detail/Wire-To-Board-Wire-To-Wire-Connector_BOOMELE-Boom-Precision-Elec-1-0T-4P_C145961.html) | JST SH4 Connector | JST SH4 RA | C145961 (https://www.lcsc.com/product-detail/Wire-To-Board-Wire-To-Wire-Connector_BOOMELE-Boom-Precision-Elec-1-0T-4P_C145961.html) |  | 0.05
2 | IC1 | 1 | Sensirion | SCD41-D-R2 (https://www.lcsc.com/product-detail/Gas-Sensors_Sensirion-SCD41-D-R2_C3659294.html) | SCD41-D-R2 Photoaccoustic CO2 Sensor | LGA-20 |  | https://www.mouser.com/ProductDetail/Sensirion/SCD41-D-R2?qs=HBWAp0VN4Ri4o7ei4T3s0g%3D%3D | 37.1 | 32.6 | 27.11
3 | SHT45 | 1 | Sensirion | SHT45-AD1B-R2 (https://www.lcsc.com/product-detail/Temperature-Sensors_Sensirion-SHT45-AD1B-R2_C5221601.html) | SHT45-AD1B-R2 rel Humidity and Temperature Sensor | SHT45-AD1B-R2 |  | https://www.mouser.com/ProductDetail/Sensirion/SHT45-AD1B-R2?qs=Znm5pLBrcAImXcmTJwn%2FTg%3D%3D | 7.18 | 4.55 | 4.41
4 | U1 | 1 | Sensirion | SGP41-D-R4 (https://www.lcsc.com/product-detail/Gas-Sensors_Sensirion-SGP41-D-R4_C3659325.html) | SGP41-D-R4 VOC, NOx Sensor | DFN-6 | C3659325 (https://www.lcsc.com/product-detail/Gas-Sensors_Sensirion-SGP41-D-R4_C3659325.html) | https://www.mouser.com/ProductDetail/Sensirion/SGP41-D-R4?qs=A6eO%252BMLsxmRqwfOE5NYPVA%3D%3D | 8.96 | 6.64 | 5.71
5 | U2 | 1 | Amphenol ICC | MICS-6814 (https://www.lcsc.com/product-detail/Gas-Sensors_Amphenol-ICC-MICS-6814_C3659383.html) | MICS-6814 CO, NOx, NH3 Sensor | MICS-6814 |  | https://www.mouser.com/ProductDetail/Amphenol-SGX-Sensortech/MICS-6814?qs=YCa%2FAAYMW01pNK%252BnW3Jo7g%3D%3D | 11.39 | 9.03 | 7.01
6 | U3 | 1 | Bosch Sensortec | BMP581 | BMP581 Atmospheric Pressure Sensor | LGA-10 |  | https://www.mouser.com/ProductDetail/Bosch-Sensortec/BMP581?qs=Li%252BoUPsLEntPL9tlFmcgXg%3D%3D | 4.12 | 2.61 | 2.53
7 | U4 | 1 | Diodes Incorporated | AP22802AW5-7K-3.3V | AP22802AW5-7K-3.3V, Single Channel Power Distribution Switch | SOT-25 |  | https://www.mouser.com/ProductDetail/Diodes-Incorporated/AP22802AW5-7?qs=4WD8WRWcnWuvM%252B9XDtDpnA%3D%3D | 0.31 | 0.214 | 0.101
8 | U5 | 1 | Diodes Incorporated | AP3602AKTR-G1 | AP3602AKTR-G1 100mA 3 to 5 V Boost Converter | SOT-26-6 |  | https://www.mouser.com/ProductDetail/Diodes-Incorporated/AP3602AKTR-G1?qs=5V6w%252Be2aIqZe7SZnxovZqw%3D%3D | 0.48 | 0.379 | 0.287
9 | LED0, LED1, LED2, LED3, LED4, LED5, LED6, LED7, LED8, LED9, LED10, LED11 | 12 | XINGLIGHT | XL-2020RGBC-WS2812B (https://www.lcsc.com/product-detail/Light-Emitting-Diodes-LED_XINGLIGHT-XL-2020RGBC-WS2812B_C5349955.html) | RGB LED WS2812B 2x2mm | XL-2020RGBC-WS2812B | C5349955 (https://www.lcsc.com/product-detail/Light-Emitting-Diodes-LED_XINGLIGHT-XL-2020RGBC-WS2812B_C5349955.html) |  | 0.078
10 | D1 | 1 | XINGLIGHT | XL-1608UBC-04 (https://www.lcsc.com/product-detail/Light-Emitting-Diodes-LED_XINGLIGHT-XL-1608UBC-04_C965807.html) | Blue LED 0603 | 0603 | C965807 (https://www.lcsc.com/product-detail/Light-Emitting-Diodes-LED_XINGLIGHT-XL-1608UBC-04_C965807.html) |  | 0.0034
11 | R1, R2 | 2 | YAGEO | RC0603FR-074K7L (https://www.lcsc.com/product-detail/Chip-Resistor-Surface-Mount_YAGEO-RC0603FR-074K7L_C99782.html) | 4.7K | 0603 | C99782 (https://www.lcsc.com/product-detail/Chip-Resistor-Surface-Mount_YAGEO-RC0603FR-074K7L_C99782.html)
12 | R3 | 1 | YAGEO | RC0603JR-070RL (https://www.lcsc.com/product-detail/Chip-Resistor-Surface-Mount_YAGEO-RC0603JR-070RL_C95177.html) | 0 | 0603 | C95177 (https://www.lcsc.com/product-detail/Chip-Resistor-Surface-Mount_YAGEO-RC0603JR-070RL_C95177.html)
13 | R4, R5, R6 | 3 | YAGEO | RC0603FR-074R7L (https://www.lcsc.com/product-detail/Chip-Resistor-Surface-Mount_YAGEO-RC0603FR-074R7L_C137705.html) | 4.7 | 0603 | C137705 (https://www.lcsc.com/product-detail/Chip-Resistor-Surface-Mount_YAGEO-RC0603FR-074R7L_C137705.html)
14 | R7, R15 | 2 | YAGEO | RC0603FR-0710KL (https://www.lcsc.com/product-detail/Chip-Resistor-Surface-Mount_YAGEO-RC0603FR-0710KL_C98220.html) | 10K | 0603 | C98220 (https://www.lcsc.com/product-detail/Chip-Resistor-Surface-Mount_YAGEO-RC0603FR-0710KL_C98220.html)
15 | R8 | 1 | YAGEO | RC0603FR-0730RL (https://www.lcsc.com/product-detail/Chip-Resistor-Surface-Mount_YAGEO-RC0603FR-0730RL_C128060.html) | 30 | 0603 | C128060 (https://www.lcsc.com/product-detail/Chip-Resistor-Surface-Mount_YAGEO-RC0603FR-0730RL_C128060.html)
16 | R9 | 1 | YAGEO | RT0603BRD0739RL (https://www.lcsc.com/product-detail/Chip-Resistor-Surface-Mount_YAGEO-RT0603BRD0739RL_C861370.html) | 39 | 0603 | C861370 (https://www.lcsc.com/product-detail/Chip-Resistor-Surface-Mount_YAGEO-RT0603BRD0739RL_C861370.html)
17 | R10 | 1 | YAGEO | RC0603FR-0760R4L (https://www.lcsc.com/product-detail/Chip-Resistor-Surface-Mount_YAGEO-RC0603FR-0760R4L_C245987.html) | 60.4 | 0603 | C245987 (https://www.lcsc.com/product-detail/Chip-Resistor-Surface-Mount_YAGEO-RC0603FR-0760R4L_C245987.html)
18 | R11 | 1 | YAGEO | RC0603FR-071M21L (https://www.lcsc.com/product-detail/Chip-Resistor-Surface-Mount_YAGEO-RC0603FR-071M21L_C482621.html) | 1.21M | 0603 | C482621 (https://www.lcsc.com/product-detail/Chip-Resistor-Surface-Mount_YAGEO-RC0603FR-071M21L_C482621.html)
19 | R12 | 1 | YAGEO | RC0603FR-0730K1L (https://www.lcsc.com/product-detail/Chip-Resistor-Surface-Mount_YAGEO-RC0603FR-0730K1L_C137745.html) | 30.1k | 0603 | C137745 (https://www.lcsc.com/product-detail/Chip-Resistor-Surface-Mount_YAGEO-RC0603FR-0730K1L_C137745.html)
20 | R13 | 1 | YAGEO | RC0603FR-0747KL (https://www.lcsc.com/product-detail/Chip-Resistor-Surface-Mount_YAGEO-RC0603FR-0747KL_C105579.html) | 47k | 0603 | C105579 (https://www.lcsc.com/product-detail/Chip-Resistor-Surface-Mount_YAGEO-RC0603FR-0747KL_C105579.html)
21 | R14 | 1 | YAGEO | RC0603FR-07330RL (https://www.lcsc.com/product-detail/Chip-Resistor-Surface-Mount_YAGEO-RC0603FR-07330RL_C105881.html) | 330 | 0603 | C105881 (https://www.lcsc.com/product-detail/Chip-Resistor-Surface-Mount_YAGEO-RC0603FR-07330RL_C105881.html)
22 | R16 | 1 | YAGEO | RC0603FR-071KL (https://www.lcsc.com/product-detail/Chip-Resistor-Surface-Mount_YAGEO-RC0603FR-071KL_C22548.html) | 1k | 0603 | C22548 (https://www.lcsc.com/product-detail/Chip-Resistor-Surface-Mount_YAGEO-RC0603FR-071KL_C22548.html)
23 | C1, C4, C8, C10, C16 | 5 | Samsung Electro-Mechanics | CL10B104KB8NNNC (https://www.lcsc.com/product-detail/Multilayer-Ceramic-Capacitors-MLCC-SMD-SMT_Samsung-Electro-Mechanics-CL10B104KB8NNNC_C1591.html) | 0.1UF | 0603 | C1591 (https://www.lcsc.com/product-detail/Multilayer-Ceramic-Capacitors-MLCC-SMD-SMT_Samsung-Electro-Mechanics-CL10B104KB8NNNC_C1591.html)
24 | C12, C13, C14, C15, C17, C18, C19, C20, C21, C22, C23, C24 | 12 | Samsung Electro-Mechanics | L05B104KO5NNNC (https://www.lcsc.com/product-detail/Multilayer-Ceramic-Capacitors-MLCC-SMD-SMT_Samsung-Electro-Mechanics-CL05B104KO5NNNC_C1525.html) | 0.1UF | 0402 | C1525 (https://www.lcsc.com/product-detail/Multilayer-Ceramic-Capacitors-MLCC-SMD-SMT_Samsung-Electro-Mechanics-CL05B104KO5NNNC_C1525.html)
25 | C2, C3, C5, C6, C7 | 5 | Samsung Electro-Mechanics | CL10A105KB8NNNC (https://www.lcsc.com/product-detail/Multilayer-Ceramic-Capacitors-MLCC-SMD-SMT_Samsung-Electro-Mechanics-CL10A105KB8NNNC_C15849.html) | 1.0UF | 0603 | C15849 (https://www.lcsc.com/product-detail/Multilayer-Ceramic-Capacitors-MLCC-SMD-SMT_Samsung-Electro-Mechanics-CL10A105KB8NNNC_C15849.html)
26 | C25 | 1 | Samsung Electro-Mechanics | CL05A105KP5NNNC (https://www.lcsc.com/product-detail/Multilayer-Ceramic-Capacitors-MLCC-SMD-SMT_Samsung-Electro-Mechanics-CL05A105KP5NNNC_C14445.html) | 1.0UF | 0402 | C14445 (https://www.lcsc.com/product-detail/Multilayer-Ceramic-Capacitors-MLCC-SMD-SMT_Samsung-Electro-Mechanics-CL05A105KP5NNNC_C14445.html)
27 | C9, C11, C26, C27 | 4 | Samsung Electro-Mechanics | CL10A106MA8NRNC (https://www.lcsc.com/product-detail/Multilayer-Ceramic-Capacitors-MLCC-SMD-SMT_Samsung-Electro-Mechanics-CL10A106MA8NRNC_C96446.html) | 10UF | 0603 | C96446 (https://www.lcsc.com/product-detail/Multilayer-Ceramic-Capacitors-MLCC-SMD-SMT_Samsung-Electro-Mechanics-CL10A106MA8NRNC_C96446.html)
99 | SEN50 | 1 | Sensirion | SEN50-SDN-T (https://www.lcsc.com/product-detail/Gas-Sensors_Sensirion-SEN50-SDN-T_C7000490.html) | SEN50 Particulate Matter Sensor | SEN50-SDN-T | C7000490 (https://www.lcsc.com/product-detail/Gas-Sensors_Sensirion-SEN50-SDN-T_C7000490.html) | https://www.mouser.com/ProductDetail/Sensirion/SEN50-SDN-T?qs=MyNHzdoqoQK%2F9NY8sYsxtw%3D%3D | 22.18 | 18.94 | 15.75
 |  |  |  |  |  |  |  |  | 91.8514 | 74.963 | 62.908

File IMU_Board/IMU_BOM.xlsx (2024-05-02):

Item # | Comment | Designator | Footprint | Part # LCSC or U.S. | Cost | Cost 10 | Cost 100
1 | 0.1UF | C1, C2, C3, C4, C5, C13, C17 | 0603 | C1591 (https://www.lcsc.com/product-detail/Multilayer-Ceramic-Capacitors-MLCC-SMD-SMT_Samsung-Electro-Mechanics-CL10B104KB8NNNC_C1591.html)
2 | 1.0UF | C15, C16 | 0603 | C15849 (https://www.lcsc.com/product-detail/Multilayer-Ceramic-Capacitors-MLCC-SMD-SMT_Samsung-Electro-Mechanics-CL10A105KB8NNNC_C15849.html)
3 | 10UF | C14, C21 | 0603 | C96446 (https://www.lcsc.com/product-detail/Multilayer-Ceramic-Capacitors-MLCC-SMD-SMT_Samsung-Electro-Mechanics-CL10A106MA8NRNC_C96446.html)
4 | 10Ω | R5, R6, R7, R8, R9, R10, R14, R27, R28 | 0603 | C109317 (https://www.lcsc.com/product-detail/Chip-Resistor-Surface-Mount_YAGEO-RC0603JR-0710RL_C109317.html)
5 | 10kΩ | R1, R2, R3, R4, R11, R12, R13, R15, R17, R18, R19, R20, R21, R22, R23, R24, R25 | 0603 | C98220 (https://www.lcsc.com/product-detail/Chip-Resistor-Surface-Mount_YAGEO-RC0603FR-0710KL_C98220.html)
6 | 1kΩ | R16 | 0603 | C22548 (https://www.lcsc.com/product-detail/Chip-Resistor-Surface-Mount_YAGEO-RC0603FR-071KL_C22548.html)
7 | AP2112K-1.8TRG | U4 | SOT 25 | C176944 (https://www.lcsc.com/product-detail/Linear-Voltage-Regulators-LDO_Diodes-Incorporated-AP2112K-1-8TRG1_C176944.html)
8 | BMP581 Pressure | U3 | LGA-10 | https://www.mouser.com/ProductDetail/Bosch-Sensortec/BMP581?qs=Li%252BoUPsLEntPL9tlFmcgXg%3D%3D | 4.12 | 2.61 | 2.53
9 | MOSFET-NCHANNEL | Q1, Q2, Q3, Q4, Q5 | SOT23-3 | C82045 (https://www.lcsc.com/product-detail/MOSFETs_onsemi-BSS138LT1G_C82045.html)
10 | ICM-20948 IMU 9-Axis | U1 | QFN-24 | https://www.mouser.com/ProductDetail/TDK-InvenSense/ICM-20948?qs=u4fy%2FsgLU9OtGc31yF%2Friw%3D%3D | 8.32 | 6.38 | 5.45
11 | Blue LED | D1 | 0603 | C965807 (https://www.lcsc.com/product-detail/Light-Emitting-Diodes-LED_XINGLIGHT-XL-1608UBC-04_C965807.html)
 |  |  |  |  | 12.44 | 8.99 | 7.98

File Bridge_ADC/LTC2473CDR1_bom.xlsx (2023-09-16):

Item # | *Designator | *Qty | Manufacturer | *Mfg Part # | Description / Value | *Package/Footprint | Type | Your Instructions / Notes
1 | C1, C2, C3, C4, C5, C7, C8, C9, C10, C11 | 10 | Murata Electronics | GRM188R72A104KA35J | CAP 0.1uF 10V | 603 | SMD | LCSC 0.1UF-0603-10V
2 | R1, R2, R3, R4, R5, R6, R7, R8 | 8 | YAGEO | RC0603FR-0710KL | RES 10k 0603 1/10W 1% | 603 | SMD | LCSC 10KOHM-0603-1/10W-1%
3 | C6, C12 | 2 | Murata Electronics | GRM188R61A106KE69D | CAP 10uF 10V | 603 | SMD | LCSC 10UF-0603-10V
4 | R16 | 1 | YAGEO | RE0603FRE071KL | RES 1k 0603 1/10W 1% | 603 | SMD | LCSC 1KOHM-0603-1/10W-1%
5 | J1 | 1 | TE Connectivity AMP Connectors | 282834-4 | TERM BLK 4P SIDE ENT 2.54MM PCB | 2.54mm | thru-hole | 4 Position Wire to Board Terminal Block Horizontal with Board 0.100" (2.54mm) Through Hole 10.3mm height
7 | D1 | 1 | Lite-On | LTST-C190KGKT | GREEN LED SMD 2V | 603 | SMD | LCSC Green LED
8 | U1, U2 | 2 | Analog Devices | LTC2473IMS#PBF | IC ADC 16BIT SIGMA-DELTA 12MSOP | MSOP-12 | SMD | 16 Bit Analog to Digital Converter 1 Input 1 Sigma-Delta 12-MSOP
9 | J3, J4 | 2 | JST | SM04B-SRSS-TB | JST SH CONN HEADER SMD R/A 4POS 1MM | JST04_1MM_RA | SMD | QWIIC connector

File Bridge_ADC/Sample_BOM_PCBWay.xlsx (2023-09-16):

 |  |  | xxxx xxxx xxxxx xxPCS BOM (Sample Bill of Materials)
Item # | *Designator | *Qty | Manufacturer | *Mfg Part # | Description / Value | *Package/Footprint | Type | Your Instructions / Notes
1 | U1 | 1 | Linear | LTC3780EG#PBF | IC BUCK-BOOST CONV 24-SSOP | 24-SSOP | SMD
2 | U2,U4 | 2 | Fairchild | LM2904M | IC OPAMP DUAL -40-85 C 8-SOIC | 8-SOIC | DNS
3 | U3 | 1 | ON | LM317MBDTG | LM317M IC REG VOLT ADJ 500MA DPAK | DPAK | SMD
4 | U5 | 1 | Microchip | PIC16F690-I/SS | IC PIC MCU FLASH 4KX14 20SSOP | 20SSOP | SMD
5 | Q1 | 1 | Diodes Inc | GBJ10005-F | RECT BRIDGE GPP 50V 10A GBJ | GBJ | SMD
6 | R14,R18 | 2 | Panasonic | ERJ-6ENF4701V | RES 4.70K OHM 1/8W 1% 0805 SMD | 0805 | SMD
7 | R15 | 1 | Susumu | RL3720WT-R022-F | RES .022 OHM 1W 1% 0815 SMD | 0815 | SMD
8 | R16, R31 | 2 | Panasonic | ERJ-6ENF4702V | RES 47.0K OHM 1/8W 1% 0805 SMD | 0805 | SMD
9 | C5 | 1 | Murata | GRM21BR71C225KA12L | CAP CER 2.2UF 16V X7R 0805 | 0805 | SMD
10 | C7 | 1 | Murata | GRM21BR71C475KA73L | CAP CER 4.7UF 16V X7R 0805 | 0805 | DNS
11 | C8,C22 | 2 | Muruta | GRM21BR71C105KA01L | CAP CER 1.0UF 16V 10% X7R 0805 | 0805 | SMD
12 | CN6 | 1 | Molex | 538-53398-0671 | 1.25mm Connectors VERTICAL HDR SMT 6P | SMT 6P | SMD
13 | L1,L2 | 2 | Coiltronics | DR127-150-R | INDUCTOR SHIELD PWR 15UH SMD | SMD | SMD
14 | L3 | 1 | TDK | ACM1211-102-2PL-TL | CHOKE COMM MODE 1000 OHM 6A SM | SMD | SMD
15 | CN3,CN4 | 2 | Molex | 53047-0510 | CONN HEADER 5POS 1.25MM VERT TIN | 5POS | thru-hole
Need a quick and accurante quote? Need an efficient production? Please read SMT Ordering Necessary Files & Info in 1 minute. Thank you very much! (https://www.pcbway.com/smt_ordering_guide.html)
Click for Instructions on How to Create a BOM (https://www.pcbway.com/blog/PCB_Assembly/How_to_Build_a_BOM__Bill_Of_Materials_.html)

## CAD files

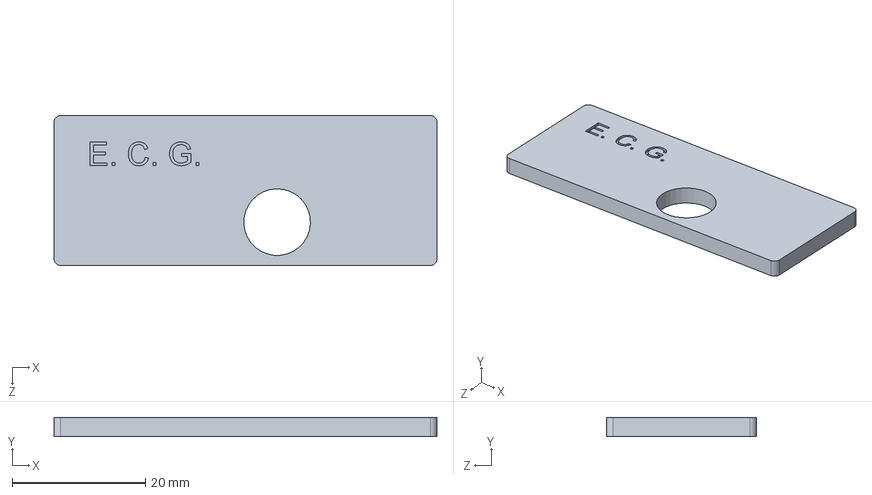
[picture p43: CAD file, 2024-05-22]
ECG_Board/Insert/Part 100750.SLDPRT
57.5 x 2.90 x 22.5 mm

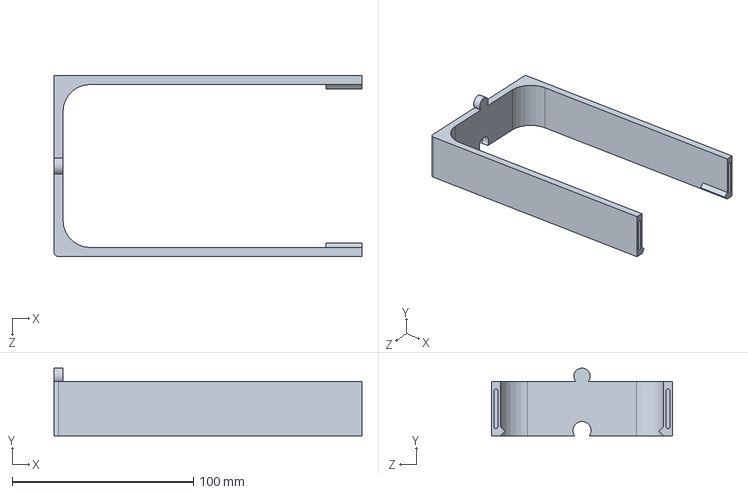
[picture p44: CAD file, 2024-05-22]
Housing Models/Charging Station/Part 100251 Surpise Addon.SLDPRT
170.0 x 37.5 x 100.0 mm

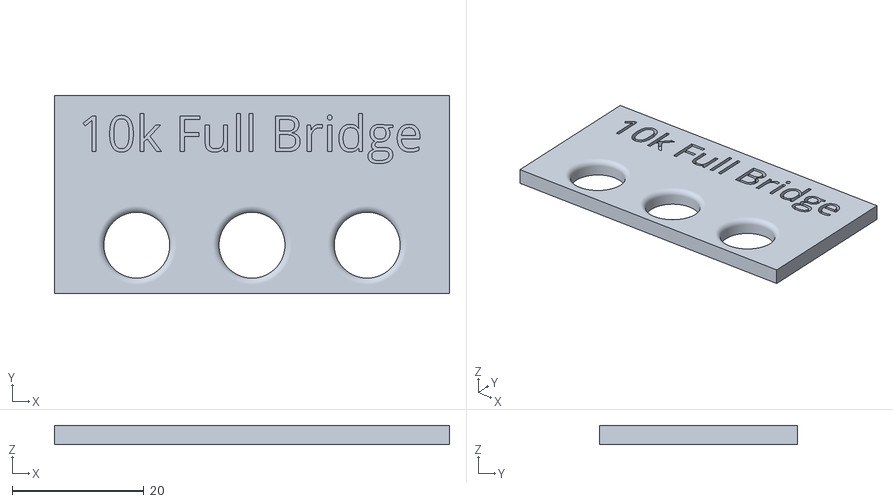
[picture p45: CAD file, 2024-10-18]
Housing Models/Face Plates/Face Plate - Temperature.stl
60.0 x 30.0 x 2.90

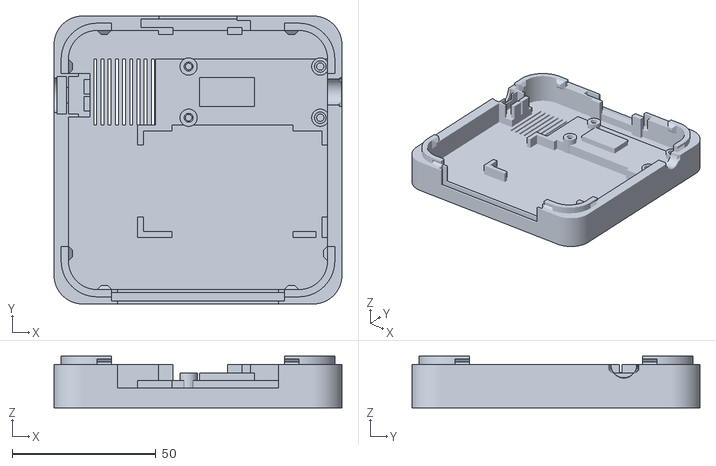
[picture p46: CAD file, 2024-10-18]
Housing Models/Module Casing/MicroController and Battery.stl
100.0 x 100.0 x 18.0

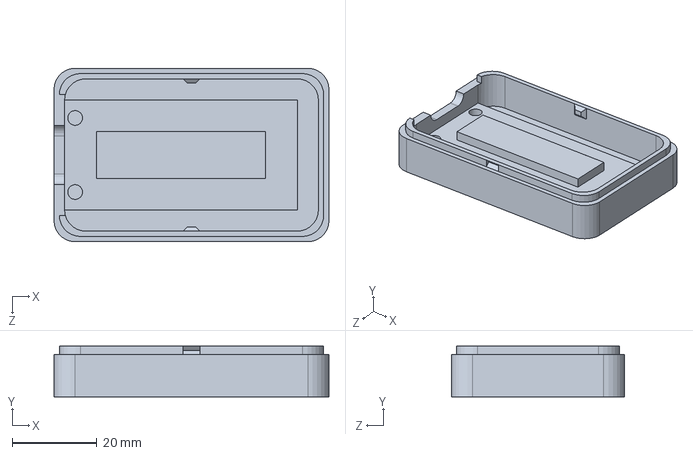
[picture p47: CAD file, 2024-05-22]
Housing Models/Receiver Casing/Part 100230.SLDPRT
65.0 x 12.0 x 41.0 mm

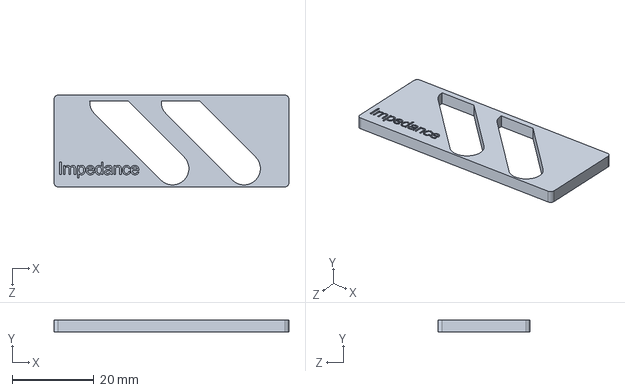
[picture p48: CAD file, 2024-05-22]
Impedance_Board/Insert/Part 100660.SLDPRT
57.5 x 2.90 x 22.5 mm

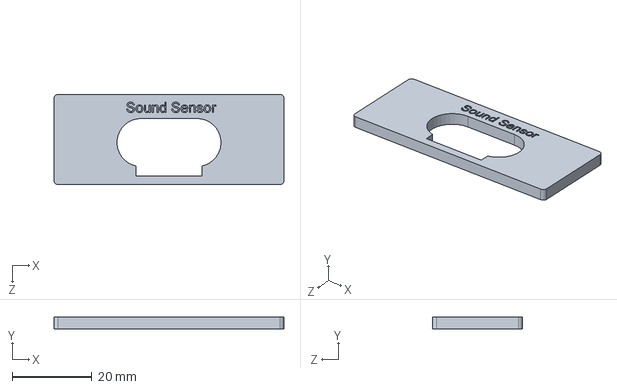
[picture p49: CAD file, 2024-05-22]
Stethoscope_with_3rdparty_Sound/Insert/Part 100460.SLDPRT
57.5 x 2.90 x 22.5 mm

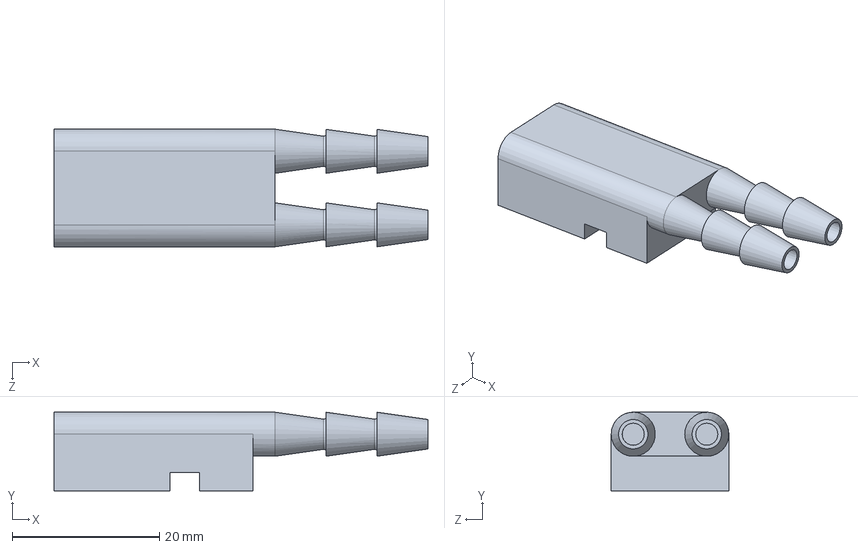
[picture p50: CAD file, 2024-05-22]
Stethoscope_with_3rdparty_Sound/Plug for Stethoscope/Part 100450.SLDPRT
50.9 x 10.7 x 16.0 mm

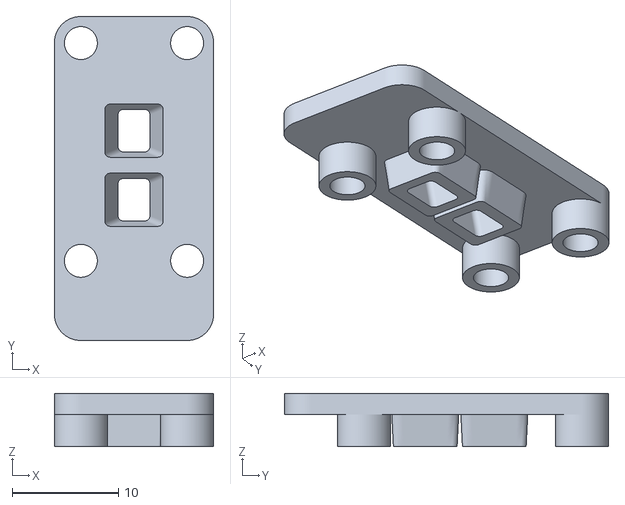
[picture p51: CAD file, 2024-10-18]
Stethoscope_with_Pressure/Models/Microphone-Bottom.stl
15.0 x 30.5 x 5.00

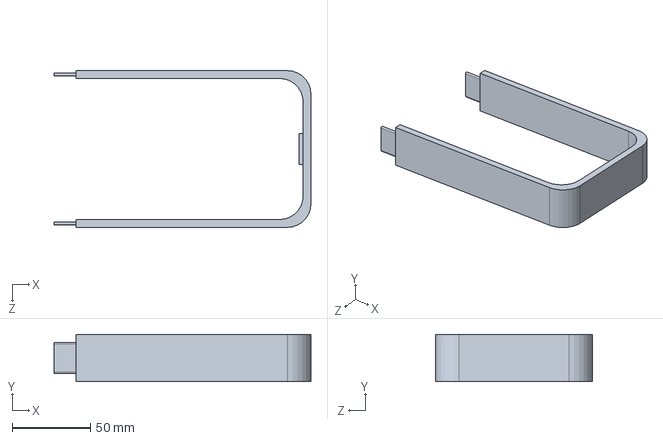
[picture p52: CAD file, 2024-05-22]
Housing Models/Charging Station/Part 100252 Surpise Addon.SLDPRT
164.0 x 30.0 x 100.0 mm

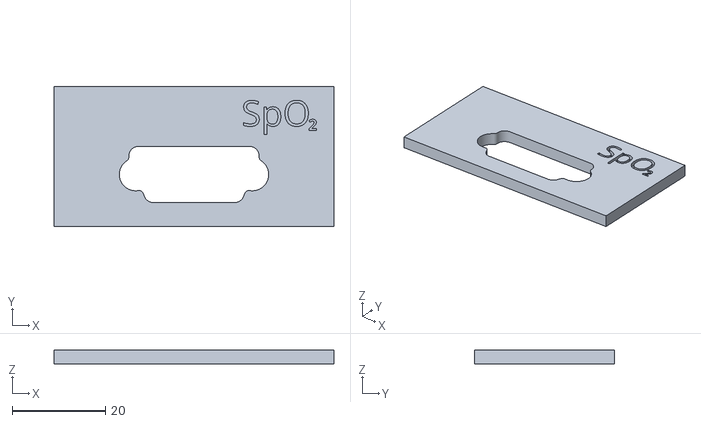
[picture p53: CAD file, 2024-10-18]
Housing Models/Face Plates/Face Plate - SpO2.stl
60.0 x 30.0 x 2.90

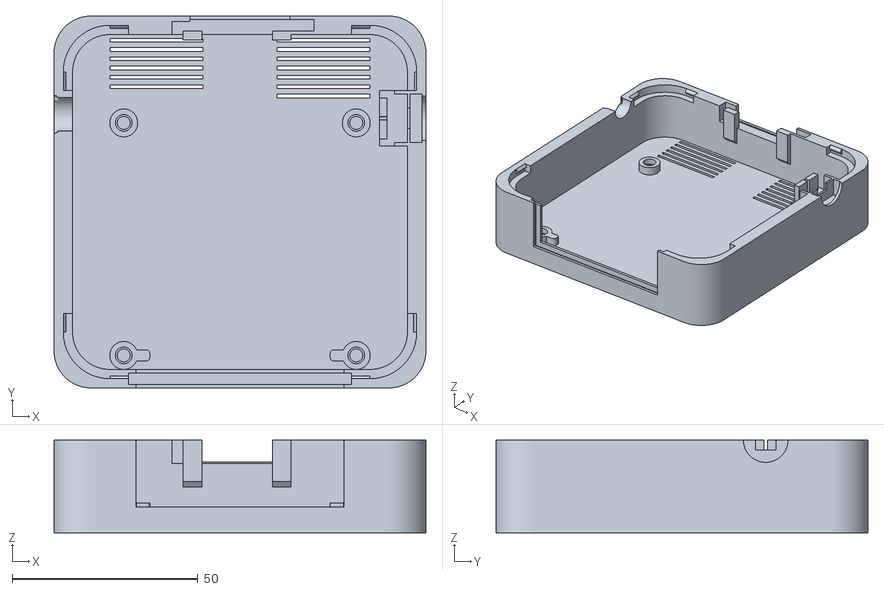
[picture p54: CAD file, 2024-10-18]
Housing Models/Module Casing/Board.stl
100.0 x 100.0 x 25.0

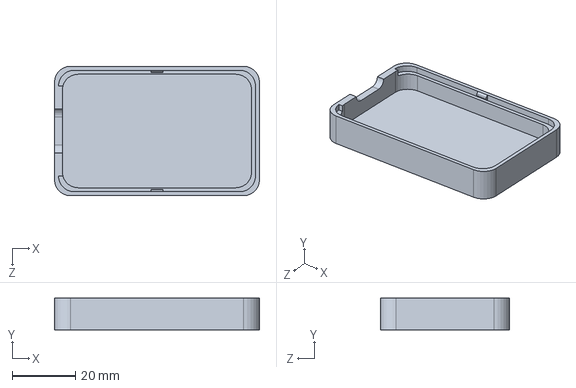
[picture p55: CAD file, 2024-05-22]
Housing Models/Receiver Casing/Part 100240.SLDPRT
65.0 x 10.0 x 41.0 mm

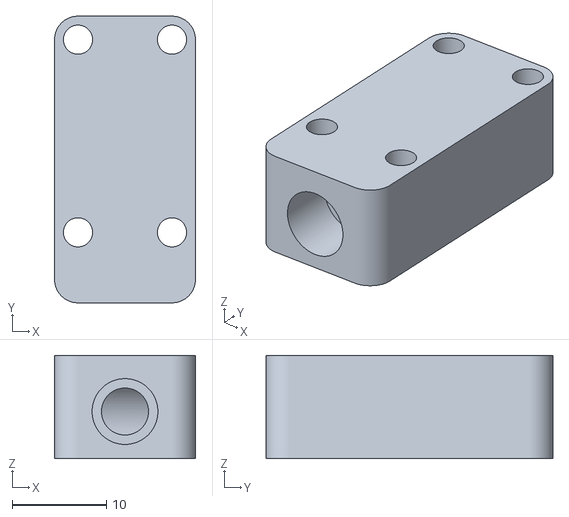
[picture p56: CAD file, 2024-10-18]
Stethoscope_with_Pressure/Models/Microphone-Top.stl
15.0 x 30.5 x 11.0

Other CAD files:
Thermistor_Board/using_MicroController_ADC/Insert/Part 100340.SLDPRT
Housing Models/Charging Station/Part 100260.SLDPRT
Housing Models/Face Plates/Face Plate - Stethoscope.stl
Housing Models/Module Casing/Part 100220_mk3.SLDPRT
ECG_Board/Insert/Part 100750.STL
Housing Models/Charging Station/Part 100250.SLDPRT
Housing Models/Charging Station/Part 100250.STL
Housing Models/Charging Station/Part 100251 Surpise Addon.STL
Housing Models/Charging Station/Part 100252 Surpise Addon.STL
Housing Models/Charging Station/Part 100260.STL
Housing Models/Face Plates/Face Plate - BioZ.stl
Housing Models/Face Plates/Face Plate - Environment.stl
Housing Models/Face Plates/Face Plate - IMU.stl
Housing Models/Face Plates/Face Plate - Plain.stl
Housing Models/Module Casing/Part 100210_mk2.SLDPRT
Housing Models/Module Casing/Part 100210_mk2.STL
Housing Models/Module Casing/Part 100220_mk3.STL
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

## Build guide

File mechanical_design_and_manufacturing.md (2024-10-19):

# Mechanical Design and Manufacturing

All models in this project have been designed in OnShape. OnShape has a free academic license. Without an account you can still view the models. STL files are provided in the project. STL is a surface model and usually is not made to be edited. Although programs claim that you can export and convert into other formats, most export does not include your design process and you can not easily change the length or diameter of a component of an imported file.

The mechanical designs are not space optimized. They have beefy wall thickness and can accomodate larger items and more complex designs if necessary. They are robust for a classroom setting. All enclosures have the same size and all projects fit into the same dimensioned "brick". If the size is an issue for you, several electronic boards could be reduced to half the size and if optimized the enclosure could be reduced to 1/3. Largest project is the Airquality brick and its mostly full. The smallest project is the temperature and the IMU brick.

## Converting to STL
In OnShape select the parts on the left side menu and right click on a part. Export to STL. Download the STL file.

## 3D Printing the Models
Select your Slicer software. E..g. Prusa Slicer. Your printer configuration should be properly installed. If your printer uses input shapping (fast printing) you need to use proper printer settings, e.g. each Prusa printer has seperate driver depending if the firmware on the printer is using input shaping.

Import the STL file. Rotate the model to a surface resulting in the least amount of overhang. Avoid support material if you can. Depending on your printer bed, you might need a brim.Slice the model and inspect it. Export the g-code and load it on the printer.

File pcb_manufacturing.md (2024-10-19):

# PCB Manufacturing

## Parts
- LCSC for parts in China: https://www.lcsc.com/
- Digikey for parts in USA: https://www.digikey.com/en/products/
- Mouser for parts in USA: https://www.mouser.com/electronic-components/

## PCB Manufacturing and Assembly

- [PCBWAY](https://www.pcbway.com/quotesmt.aspx)
- [JLPCP](https://jlcpcb.com/)
- [JLPCB Part List](https://jlcpcb.com/parts)

### Costs PCB Way

- Minimum number of PC Boards is 5 and costs are $45.18 for WLP this will increase by 3 times
- Minimum number for assembly is 1
- Assembly of 1 to 20 costs up to $88
- Assembly of 50 costs up to $154
- Parts costs are separate
- Through hole component creates additional assembly costs
- Shipping costs are often equivalent to a discount you receive with your order

### PCB Way Assembly Service Settings
- Turnkey
- Single pieces
- Top Side board
- Quantity (assembled) e.g. 2
- Contains sensitive components: No
- Number of unique parts: See Bill of Materials (number of individual lines)
- Number of SMD parts: Total number of parts
- Number of BGA/QFP: Parts with very small pads e.g. ICS with pads at the bottom, no legs QFN
- Through hole parts: You can solder yourself
- Board type: single pieces
- Different designs: 1
- Size: 70x70 (all boards in this project)
- Quantity 5
- Layers: 2
- Material: FR-4, TG 150-60
- Thickness 1.6
- Min spacing 6mil
- Min hole size 0.3, except for micro via boards (BIOZ)
- Soldermark: choose your color (white)
- Edge connector: No
- Surface finish: Immersion Gold
- Thickness of immersion: 1U
- Via process: tenting
- Finished copper: 1 oz
- Remove product #: No, or pay extra fee to not have PCB print their part number on the board

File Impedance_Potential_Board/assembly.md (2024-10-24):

# Assembly of ECG and BioZ Brick

<a href="..\assets\pictures\ECG_BIOZ_Top_Open_without_Plugins.jpg" target="_blank">
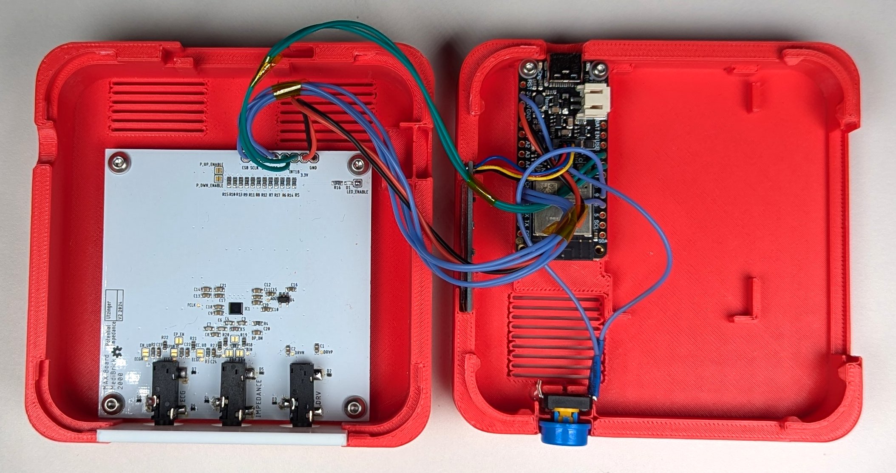
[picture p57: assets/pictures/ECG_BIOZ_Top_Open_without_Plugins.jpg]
  
</a>

## Soldering

### 3.5mm Connector
Firmly press the 3.5mm connector into the holes and solder all three pins.

### Wires
Attach color coded wires to the IO pads. E.g. red for power, black or green for ground and blue or white for digital input/output.

You can insert the wires into the holes (perpendicular) or or you can attach a short piece of the wires on top of the pad (perpendicular).

Suggested connecctions for the Sparkfun Thing Plus (USB-C) and the Adafruit Feather ESP32-S3 are below:

PAD       | Function                  | Thing Plus  | Feather
---       |---                        |---          |---
**VCC**   | Power                     | 3V3         | 3V3 
**GND**   | Power                     | GND         | GND
**CS0**   | Chip Select               | 08   GPIO15 | 6
**SDI***  | Master Out Slave In       | PICO GPIO23 | MO
**SDO***  | Master In Salve Out       | POCI GPIO19 | MI
**SCL**   | Serial Clock              | SCK  GPIO18 | SCK
**INTB**  | Interrupt Output          | 12   GIPO12 | 12 GPIO12
INT2B     | Interrupt 2 Output        | 11   GIPO27 | 13 GPIO13

Pin 10 (Feather, Thing Plus)  is reserved for system button.
Require connections are in **bold**.

*The MAX30001G Analog Front End uses the MOSI and MISO on diagrams showing a microcontroller. POCI and PICO should be used for "peripheral out controller in" and "peripheral in controller out".

## Board Configuration

There are many configurations we can select. We can operate the board to measure ECG or Impedance or both. We can operate the board to use only two leads, four leads or six leads. We can configure the board to measure impedance of a calibration resistor that is soldered onto the board (100 Ohm).

### Jumpers

<a href="./Design.svg" target="_blank">
  
</a>

There are 4 sets of jumper:

1) The following jumpers are available to reduce the numnber of required leads. They create direct conenction between the pins of the plug and the chip IO:

    For single plug operation ECG&BioZ
    - $ECG_N$ to $BI_N$
    - $ECG_P$ to $BI_P$

    For single plug BioZ operation
    - $DRV_N$ to $BI_N$
    - $DRV_P$ to $BI_P$

2) The unbalance filters for Input and Offset can be bypassed. Those are the two input pins for ECG, Bioimedance and VCM :

    - $VCM_{UB}$: $VCM$ unbalance bypass
    - $EN_{UB}$: $ECG_N$ unbalance bypass
    - $EP_{UB}$: $ECG_P$ unbalance bypass

3) We can also disable input:

    - $ECG_P$ to $ECG_N$ (this shorts N and P terminal together, for BIOZ measurements only operation)
    - $BI_P$ to $BI_N$ (this shorts N and P terminal together, for ECG measurements only operation)

4) We can calibrate BIOZ with a 100 Ohm resistor:

    - $R_N$, $R_P$ connect $BI_N$, $BI_P$ to 100 Ohm (R18), for testing purose only, once conencted no external impedance can be measured.

If $V_{CM}$ is used for ECG right leg bias, internal lead bias needs to be disabled. Resistor can be 10k..200kOhm.

For specific hardware configuration setup the following jumpers should be set:

### Configuration Options

Configuration          | $ECG_P$ to $ECG_N$ | $DRV_N$ to $BI_N$ | $DRV_P$ to $BI_P$ | $ECG_N$ to $BI_N$ | $ECG_P$ to $BI_P$ | $R_N$ | $R_P$ | $VCM_{UB}$ | $EN _{UB}$ | $EP_{UB}$ |
-----------------------|--------------------|-------------------|-------------------|-------------------|-------------------|-------|-------|------------|------------|-----------|
(1) 100 Ohm Test       |                    | X                 | X                 |                   |                   | X     | X     |            |            |           | 
(2) ECG, R to R        |                    |                   |                   |                   |                   |       |       | *          |            |           | 
(3) ECG & Resp 2 leads |                    | X                 | X                 | X                 | X                 |       |       | *          |            |           | 
(4) ECG & Resp 4 leads |                    |                   |                   | X                 | X                 |       |       | *          |            |           | 
(5) GSR                | X                  | X                 | X                 |                   |                   |       |       |            |            |           | 
(6) BIOZ 2 leads       | X                  | X                 | X                 | X                 | X                 |       |       |            |            |           | 
(7) BIOZ 4 leads       | X                  |                   |                   |                   |                   |       |       |            |            |           | 
(8) BIOZ & ECG 2 leads |                    | X                 | X                 | X                 | X                 |       |       | *          |            |           | 
(9) BIOZ & ECG 4 leads |                    | X                 | X                 |                   |                   |       |       | *          |            |           | 
(10) BIOZ & ECG 6 leads|                    |                   |                   |                   |                   |       |       | *          |            |           | 

(X) = solder jumper closed

(*) Might need to replace R23 with 200kOhm and enable VCM bypass by soldering the jumper close.

### Lead Connections

(1) **100 Ohm BioZ Test**

    - 100 Ohm test for Driver and Impedance (BioZ)
    - No external BIOZ leads possible
    - ECG Measurement leads on ECG connector possible
    - BioZ frequency is FMSTR/64 = 500Hz
    - Increase frequency or change internal lower filter cut off

(2) **ECG** 

    - Measurement Leads on ECG connector.

(3) **2 Leads ECG**

    - Measurement Leads on ECG connector.

(4) **4 Leads ECG**

    - Driver Leads to Driver connector.
    - Measurement Leads to ECG or Impedance connector.

(5) **GSR, no ECG**

    - Measurement Leads on Impedance connector.
    - Low current frequency generator at 125, 250 or 500Hz.
    - BIOZ analog high pass needs to be below current frequency. 
    - 220nF blocking filter inline in $DRV_P$ and $DRV_N$, other circuits might have 47nF

(6) **2 Leads Bio Z**

    - BioZ Measurement connector connected to Driver connector

(7) **4 Leads Bio Z**

    - Driver Leads to Driver connector.
    - Measurement Leads to Impedance connector.

(8) **2 leads ECG & Bio Z**

    - You can not measure simultanously but you can reconfigure in software to measure one or the other
    - BIN and ECG and DRV connected

(9) **4 leads ECG & Bio Z**

    - You can not measure simultanously but you can reconfigure in software to measure one or the other
    - ECG separate, BIN & DRV connected

(9) **6 leads ECG & Bio Z**

    - You can not measure simultanously but you can reconfigure in software to measure one or the other
    - No jumper

#### Pin Outs
- [Thing Plus C Pinout](https://cdn.sparkfun.com/assets/3/9/5/f/e/SparkFun_Thing_Plus_ESP32_WROOM_C_graphical_datasheet2.pdf)
- [ESP32 S3 Pinout](https://learn.adafruit.com/assets/110811)

<a href="../assets/ThingPlusC_PinOut.png" target="_blank"> 
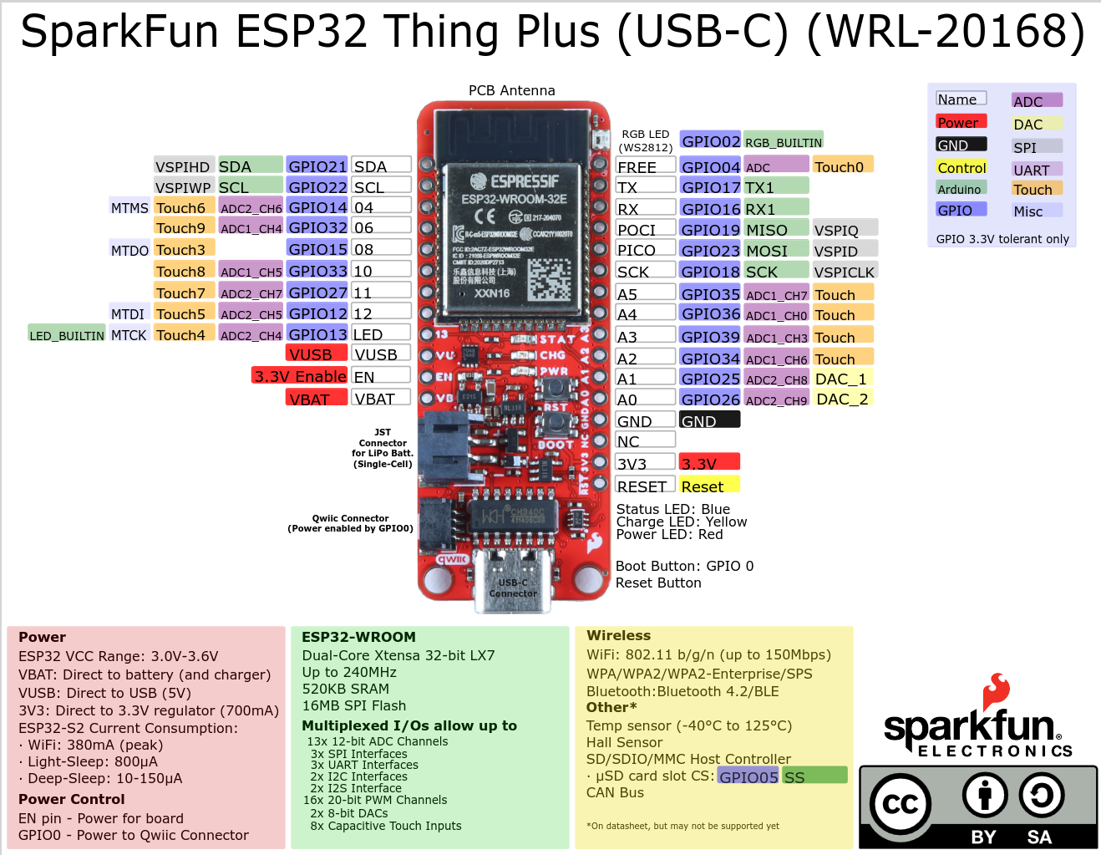
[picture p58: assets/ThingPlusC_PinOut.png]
  
</a>

<a href="../assets/adafruit_products_Adafruit_Feather_ESP32-S3_Pinout.png" target="_blank">
  
</a>

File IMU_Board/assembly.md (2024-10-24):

# Assembly of IMU Board

Two sensor, the 9 axis IMU ICM20948 and barometric pressure sensor BMP581 need to be connected. Both are communicating through SPI.
The board contains a 1.8V voltage buck to power the IMU.

<a href="..\assets\pictures\IMU_Top_Open_with_Plugins.jpg" target="_blank">
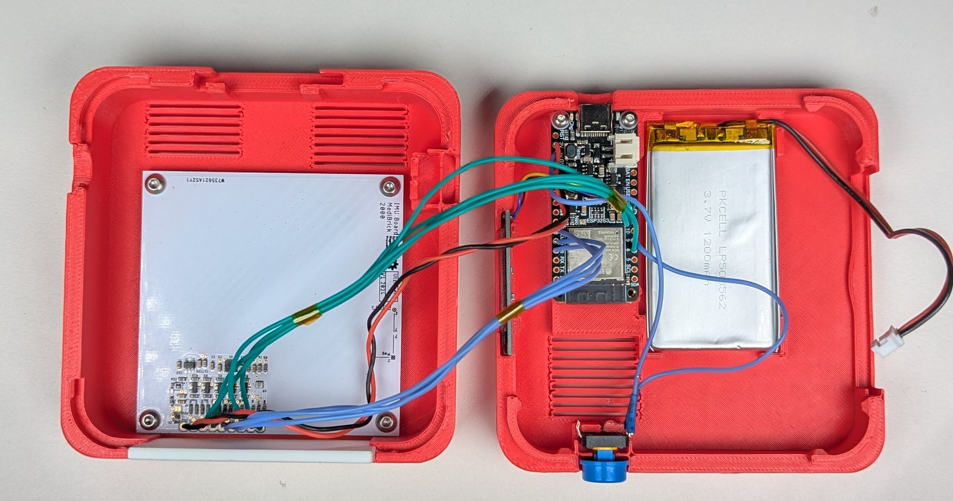
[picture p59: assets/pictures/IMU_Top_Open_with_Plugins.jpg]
  
</a>

## Soldering

Attach color coded wires to the IO pads. E.g. red for power, black or green for ground and blue or white for digital input/output and yellow for analog wires. 

You can insert the wires into the holes (perpendicular) or or you can attach a short piece of the wires on top of the pad (perpendicular).

Suggested connections for the Sparkfun Thing Plus (USB-C) and the Adafruit Feather ESP32-S3 are given below.

### Connections

PAD       | Function              | Thing Plus  | Feather
---       |---                    |---          |---
**INT5**  | BMP 581 Interrupt     | 12 GIPO12   | 12 GPIO12   
**CS5**   | BMP 581 Chip Select   | 08 GPIO15   | 6
**SDO**   | SPI PO                | POCI GPIO19 | MI
**SDI**   | SPI PI                | PICO GPIO23 | MO
**SCL**   | SPI SCL               | SCK GPIO18  | SCK
**CS2**   | ICM 20948 Chip Select | 10 GPIO33   | 11 GPIO11
**INT2**  | ICM 20948 Interrupt   | 11 GPIO27   | 13 GPIO13
**VCC**   | Power                 | 3V3         | 3V3 
**GND**   | Power                 | GND         | GND

Require connections are in **bold**.

It is important to measure each channels resistors on the PCB to achieve maximum accuracy before placing the solder bridges.
You will need those values for your software.

### Pinouts

- [Thing Plus C Pinout](https://cdn.sparkfun.com/assets/3/9/5/f/e/SparkFun_Thing_Plus_ESP32_WROOM_C_graphical_datasheet2.pdf)
- [ESP32 S3 Pinout](https://learn.adafruit.com/assets/110811)

<a href="../assets/ThingPlusC_PinOut.png" target="_blank"> 
  
</a>

<a href="../assets/adafruit_products_Adafruit_Feather_ESP32-S3_Pinout.png" target="_blank">
  
</a>

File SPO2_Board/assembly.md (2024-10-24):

# Assembly of SPO2 Board

<a href="..\assets\pictures\PulseOx_Top_Open_without_Plugins.jpg" target="_blank">
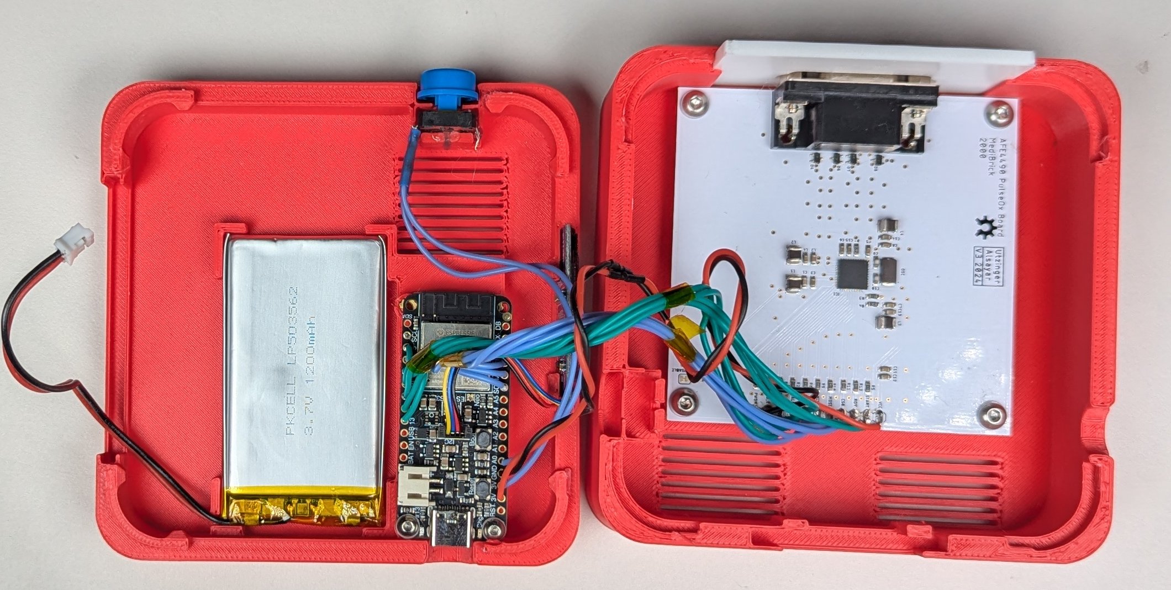
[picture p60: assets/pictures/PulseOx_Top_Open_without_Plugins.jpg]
  
</a>

## Soldering
### DB 9 Connector
Firmly press the connector into the holes and solder all pins. Add solder to the mechanical retaining hooks.
### Wires
Attach color coded wires to the IO pads.

It is not necessary to push the wires into the holes and you can simply strip a short piece of insulation and solder the wires onto the pad.

Suggested connecctions for the Sparkfun Thing Plus (USB-C) and the Adafruit Feather ESP32-S3.

PAD | Function | Thing Plus | Feather
---|---|---|---
**VCC**   | Power                     | 3V3         | 3V3 
Start     | Reset active low          | 04   GPIO14 | 10 GPIO10
**RDY**   | ADC Data Ready            | 12   GIPO12 | 13 GPIO13
**CS0**   | Chip Select               | 08   GPIO15 | 6 GPIO6
**MOSI*** | Master Out Slave In       | PICO GPIO23 | MO GPIO35
**MISO*** | Master In Salve Out       | POCI GPIO19 | MI GPIO37
**SCK**   | Serial Clokc              | SCK  GPIO18 | SCK GPIO36
D ALM     | Photo Diode Fault, Output | 06   GPIO32 | 12 GPIO12
LED ALM   | LED Cable Fault, Output   | A0   GPIO26 | 9 GPIO9, A0
DIAG_E    | Diagnostics End, Output   | 11   GPIO27 | 11 GPIO11
**PWDN**  | Power Down, active low    | A1   GPIO25 | 5 GPIO5
**GND**   | Power                     | GND         | GND

Pin 10 is reserved for system button.
Require connections are in **bold**.

*The SPO2 Aanalog Front End uses the old terminology MOSI and MISO while appropriate terminology is POCI and PICO for "peripheral out controller in" and "perpherial in controller out".

#### Button

The button is configured to pull a pin high. One button pin is connected to 3.3V and the other to the input pin on the microcontroller. In software that pin is pulled low.

PAD       | Function        | Thing Plus    | Feather
---       |---              |---            |---
**3.3V**  | Power           | 3V3           | 3V3
**Button**| Button          | 9 or A0       | 12

- [Thing Plus C Pinout](https://cdn.sparkfun.com/assets/3/9/5/f/e/SparkFun_Thing_Plus_ESP32_WROOM_C_graphical_datasheet2.pdf)
- [ESP32 S3 Pinout](https://learn.adafruit.com/assets/110811)

Thing Plus C Pinout

Adafruit Feather ESP32 S3

[Biometric Cables Pulse Ox Probe](https://www.biometriccables.in/collections/spo2-1/products/oximax-comptiable-spo2-pulse-oximeter-probe-1-0mtr)

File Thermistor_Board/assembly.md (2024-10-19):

# Assembly of Thermistor Board

<a href="..\assets\pictures\Temp_Top_Open_with_Plugins_2.jpg" target="_blank">
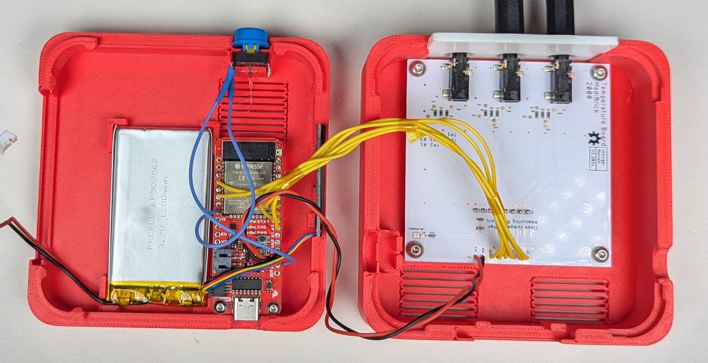
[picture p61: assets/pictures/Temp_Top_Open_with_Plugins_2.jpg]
  
</a>

## Board Recommendation

We need 6 ADC channels from ADC unit 1 exposed. Some boards use I2C pins overlaid on ADC unit 1 channels.

There is also difference in sampling rates between ESP32 models. ESP32-S3 has a maximum sampling rate of 83kHz where ESP32 has 2MHz. 

I recommend using Sparkfun Thing Plus or Thing Plus C as they have a 2MHz max sampling rate.

When setting up the Wheatstone bridge the supply voltage is about 3.3V.
If the thermistor is NTC type, resistance will decrease with temperature.
The minimum resistance is at 45C and will be 4k Ohm and the maximum at freezing about 35k.Therefore one Voltage will be constant at about 1.6V and the other between 0.9 .. 2.5V.

Therefore ADC setting for ESP32 should be chosen as following:

| Choice              | Description    | Voltage Range   |
|---------------------|----------------|-----------------|
| ADC_ATTEN_DB_0,     | No attenuation | 0.1  to 0.95 V  |
| ADC_ATTEN_DB_2_5    | 2.5 dB         | 0.1  to 1.25 V  |
| ADC_ATTEN_DB_6      |   6 dB         | 0.15 to 1.175 V |
| **ADC_ATTEN_DB_11** |  11 dB         | 0.15 to 2.45 V  |

The bridge resistors should be at a ratio of 2 to 1 so that R2 and R3 resistor are 20k and R1 is 10k. This would allow more accurate measurement of temperature in physiological range.

## Soldering

Attach color coded wires to the IO pads. E.g. red for power, black or green for ground and blue or white for digital input/output and yellow for analog wires. 

You can insert the wires into the through holes (perpendicular) or or you can attach a short piece of the wires on top of the pad (perpendicular).

Suggested connections for the Sparkfun Thing Plus (USB-C) and the Adafruit Feather ESP32-S3 are given below.

### Connections

Analog input needs to be on same ADC unit in order to use fast continuous ADC on ESP32.
On Adafruit Feather ESP32-S3 we have only 5 pins available for ADC1 and two are also used for I2C.
In addition ESP32-S3 has maximum sample rate of 83kHz where as Thing Plus ESP32 has 2MHz

PAD      | Function    | Thing Plus     | Feather
---      |---          |---             |---
**A5**   | analog CH1A | A5 ADC1-CH7    | D9  ADC1-CH8
**A4**   | analog CH1B | A4 ADC1-CH0    | D10 ADC1-CH9
**A3**   | analog CH2A | A3 ADC1-CH3    | D11 ADC1-CH4
**A2**   | analog CH2B | A2 ADC1-CH6    | D12 ADC1-CH5
**A1**   | analog CH3A | 06/32 ADC1-CH4 | not exposed  
**A0**   | analog CH3B | 10/33 ADC1-CH5 | not exposed
**GND**  | Ground      | GND            | GND
**3.3V** | Power       | 3V3            | 3V3

Require connections are in **bold**.

#### Button

The button is configured to pull a pin high. One button pin is connected to 3.3V and the other to the input pin on the microcontroller. In software that pin is pulled low.

PAD       | Function        | Thing Plus    | Feather
---       |---              |---            |---
**3.3V**  | Power           | 3V3           | 3V3
**Button**| Button          | 9 or A0       | 12

### Pinouts
- [Thing Plus C Pinout](https://cdn.sparkfun.com/assets/3/9/5/f/e/SparkFun_Thing_Plus_ESP32_WROOM_C_graphical_datasheet2.pdf)
- [ESP32 S3 Pinout](https://learn.adafruit.com/assets/110811)

<a href="../assets/ThingPlusC_PinOut.png" target="_blank"> 
  
</a>

<a href="../assets/adafruit_products_Adafruit_Feather_ESP32-S3_Pinout.png" target="_blank">
  
</a>

## Calibration

The resistors are configured the following way:



made with https://www.circuit-diagram.org/editor

The Wheatstone bridge resistors should be measured for greater accuracy.

- TP1 - TP3: R1
- TP1 - TP2: R2
- TP2 - TP3: R3

The thermistor resistance is

$R_{Thermistor} = \frac{R_3 (V_{in} R_2 - V_{diff} (R_1+R_2))}{Vin R1 + Vdiff (R_1+R_2)}$

Where $V_{diff} = V_1 - V_2$

$V_1$ and $V_2$ are measured with a microcontroller's ADC converter and they correspond to A0-A1, A2-A3 and A4-A5. ESP ADC is of low quality and linarization and averaging in software is needed.

After measuring the three resistors of each of the channels we need to close all jumpers in the circuit. There are 11 jumpers. 

## Thermistor
Amphenol 10kOhm MA100
https://www.mouser.com/datasheet/2/18/Amphenol_04022020_AAS_920_321E-1826352.pdf

| Temperature | Resistance | R_3/R_T | R_1/R_2 | R_3/R_T | R_1/R_2 |
|---          |---         |---      |---      |---      |---      |
|             |            | 10k/R_T | 10k/10k | 20k/R_T | 20k/10k |
|             |            | V_1     | V_2     | V_1     | V_2     |
| 32C         | 32739 Ohm  | 2.70 | 1.76  | 2.19 | 1.18  |
| 41C         | 25441 Ohm  | 2.53 | 1.76  | 1.97 | 1.18  |
| 50C         | 19925 Ohm  | 2.35 | 1.76  | 1.76 | 1.18  |

Illustrates that ADC_ATTEN_DB_11 and 2/1 ratio is needed between the resistors so that the measurements are in acceptable linear range of the ADC.

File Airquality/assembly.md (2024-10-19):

# Assembly of Airquality Board

<a href="..\assets\pictures\Environment_Top_Open_with_Plugins.jpg" target="_blank">
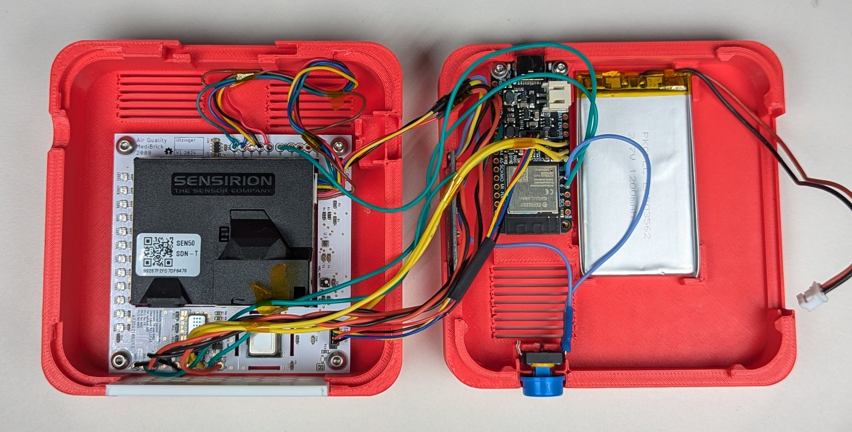
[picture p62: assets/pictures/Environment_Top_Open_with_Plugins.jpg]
  
</a>

## QWIIC Connector

PAD       | Function       | QWIIC pin | Sparkfun       | Adafruit
---       |---             |---        |---             |--- 
**GND**   | Power          | 1         | GND            | GND
**3.3**   | Power          | 2         | set GPIO0 high | I2C Power, enabled by setting PIN_I2C_POWER
**SDA**   | Serial Data    | 3         | GPIO21         | GPIO3 ADC1/CH2
**SCL**   | Serial Clock   | 4         | GPIO22         | GPIO4 ADC1/CH3

## Soldering

Attach color coded wires to the IO pads. E.g. red for power, black or green for ground and blue or white for digital input/output and yellow for analog wires. 

It is not necessary to push the wires into the holes and you can simply strip a short piece of insulation and solder the wires onto the pad.

Suggested connecctions for the Sparkfun Thing Plus (USB-C) and the Adafruit Feather ESP32-S3.

### Button

The button is configured to pull a pin high. One button pin is connected to 3.3V and the other to the input pin on the microcontroller. In software that pin is pulled low.

PAD       | Function        | Thing Plus    | Feather
---       |---              |---            |---
**3.3V**  | Button          | 3V3           | 3V3
**Button**| Button          | 9 or A0       | 12

### 6pin SEN5X Connector

This connector is for the Particula Matter sensor from Sensirion. I use the following premade [Sparkfun Cable](https://cdn.sparkfun.com/assets/8/7/b/c/8/ACCA-3479_Model__1_.pdf)

PAD        | Function                    | 6 pin
---        |---                          |---
**3.3-5V** | Power, 5V from AP3692 boost | 1
**GND**    | Power, GND                  | 2
**SDA**    | Serial Data                 | 3
**SCL**    | Serial Clock                | 4
**SEL**    | Interface Selection         | 5
N.C.       | Do not connect              | 6 

The SCL and SDA pins are connected to the board's QWIIC connector.

### LED Strip

PAD       | Function                  | Thing Plus  | Feather
---       |---                        |---          |---
**3.3-5** | Power                     | 3V3         | 3V3 
**GND**   | Power                     | GND         | GND
**DIN**   | Data In                   | SCK GPIO18  | A0 GPIO18

### SGX MiCS 6814 Sensor

PAD       | Function                  | Thing Plus  | Feather
---       |---                        |---          |---
**VCC**   | Power                     | 3V3         | 3V3 
**GND**   | Power                     | GND         | GND
**EN**    | Enable Regulator / Power  | 06   GPIO32 | D6
**NH3***  | Methane                   | A0 ADC2/CH9 | D11 ADC2/CH0
**CO***   | Carbon Monoxide           | A1 ADC2/CH8 | D12 ADC2/CH1
**NO2**   | Nitric Oxide              | 04 ADC2/CH6 | D13 ADC2/CH2

For tuning of the resistors and finalizing the connections refer to [MiCS6814](MICS6814_on_3V.md).
There are preset resistors as well as jumpers for each sensor. Turn on the power to MiCS and close a jumper. Measure the voltage on the sensor test point. If the voltage is outside the expected range you will need to replace the resistor.

### BMP 581 Interrupt

PAD       | Function                  | Thing Plus  | Feather
---       |---                        |---          |---
INT       | Interrupt                 | 10   GPIO35 | D10

Require connections are in **bold**.

## Pinouts

- [Thing Plus C Pinout](https://cdn.sparkfun.com/assets/3/9/5/f/e/SparkFun_Thing_Plus_ESP32_WROOM_C_graphical_datasheet2.pdf)
- [ESP32 S3 Pinout](https://learn.adafruit.com/assets/110811)

<a href="../assets/ThingPlusC_PinOut.png" target="_blank"> 
  
</a>

<a href="../assets/adafruit_products_Adafruit_Feather_ESP32-S3_Pinout.png" target="_blank">
  
</a>

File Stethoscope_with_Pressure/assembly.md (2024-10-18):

# Assembly of Stethoscope Brick

## Required Parts
- Fully Assembled Stethoscope PCB
- EPS Microcontroller, Adafruit Feather ESP32 S3 or Spakrfun Thing Plus C
- AWG 22 or AWG 24 Silicone Wire [Amazon](https://a.co/d/58djefc)
- Stainless steel tubing, 7mm OD, 5mm ID
- Stethoscope
- Inflatable arm cuff (pressure option)
- Miscellaneous parts:
  - M3 screws 20mm and nuts for PCB mount
  - M3 screws  and nuts for PCB mount
  - Tubing and adapters

The suggested stethoscope rubber tube has ID 5mm and uses a barb with 8mm OD. 

The suggested pressure cuff tube has ID 4mm and uses barb with barb 7mm OD.

- Rubber Tubing from Honeywell pressure sensor to arm cuff (2mm ID OD 4mm OD)
- Luer Lock 3/32 barbed adapter for rubber tubing from pressure sensor
- Luer Lock 5/32 barbed adapter for pressure cuff tube

## 3D Printed Parts
For the design models refer to the README file.

- Medibrick Housing
  - Sensor Housing bottom part
  - Sensor Housing top part
- Microphone Housing
  - Microphone Housing bottom part
  - Microphone Housing top part
- Side Plate

## Electronics

<a href="..\assets\pictures\Stethoscope_Top_Open_without_Plugins.jpg" target="_blank">
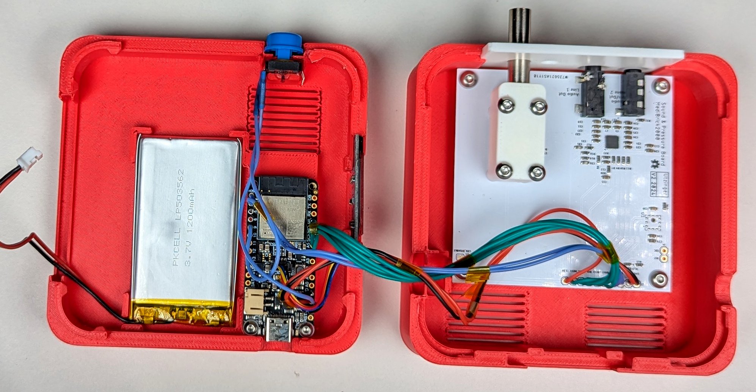
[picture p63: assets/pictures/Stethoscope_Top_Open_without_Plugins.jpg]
  
</a>

### Instructions

Attach color coded wires to the IO pads. E.g. red for power, black or green for ground and blue or white for digital input/output and yellow for analog wires. 

You can insert the wires into the holes (perpendicular) or or you can attach a short piece of the wires on top of the pad (perpendicular).

Suggested connections for the Sparkfun Thing Plus (USB-C) and the Adafruit Feather ESP32-S3 are given below.

#### Connections

PAD       | Function        | Thing Plus    | Feather
---       |---              |---            |---
**GND**   | Ground          | GND           | GND   
**3.3V**  | Power           | 3V3           | 3V3
**SDA**   | SDA / CDATA     | SDA  / GPIO21 | SDA  / GPIO3
**SCL**   | SCL / CCLK      | SCL  / GPIO22 | SCL  / GPIO4
**DOUT**  | Data Out        | POCI / GPIO19 | MISO / GPIO37
**LRCLK** | WS/Word Clock   | A5   / GPIO35 | A5   / GPIO8 / ADC1-CH7
**DIN**   | Data In / DSDIN | PICO / GPIO23 | MOSI / GPIO35
**SLCK**  | Bit Clock       | SCK  / GPIO18 | SCK  / GPIO36
**MCLK**  | Master Clock    | LED  / GPIO13 | A4   / GPIO14 / ADC2-CH3
**3.3V**  | Power           | 3V3           | 3V3

Require connections are in **bold**.

#### Button

The button is configured to pull a pin high. One button pin is connected to 3.3V and the other to the input pin on the microcontroller. In software that pin is pulled low.

PAD       | Function        | Thing Plus    | Feather
---       |---              |---            |---
**3.3V**  | Power           | 3V3           | 3V3
**Button**| Button          | 9 or A0       | 12

#### Pressure Sensor
The MPRLS0300YG end of conversion output and external reset input.

PAD       | Function          | Thing Plus | Feather
---       |---                |---         |---
**EOC**   | End of Conversion |            | D10
**RST**   | Reset             |            | D11

#### Pinouts

- [Thing Plus C Pinout](https://cdn.sparkfun.com/assets/3/9/5/f/e/SparkFun_Thing_Plus_ESP32_WROOM_C_graphical_datasheet2.pdf)
- [ESP32 S3 Pinout](https://learn.adafruit.com/assets/110811)

<a href="../assets/ThingPlusC_PinOut.png" target="_blank"> 
  
</a>

<a href="../assets/adafruit_products_Adafruit_Feather_ESP32-S3_Pinout.png" target="_blank">
  
</a>

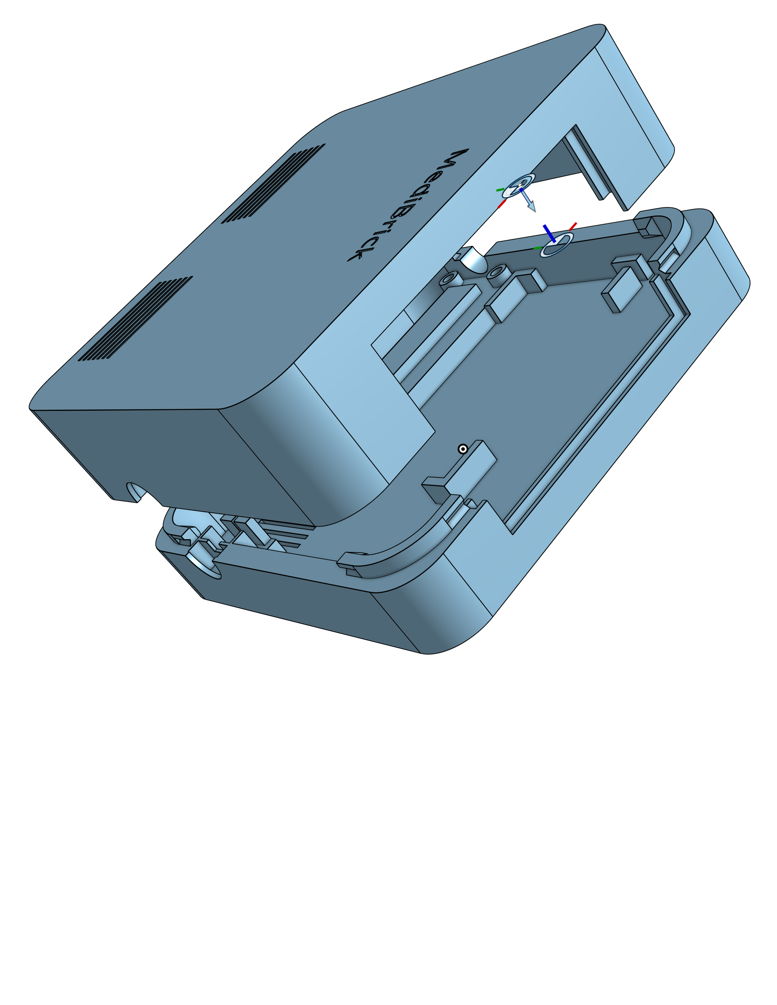
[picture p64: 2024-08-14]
Housing Models/Assembly.png

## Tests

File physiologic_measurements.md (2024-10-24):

# Common Phyiologic Measurements

**Biopotentials** are created by electric fields due to ion gradients primarily over muscle cells and neurons. Skin resistance is attenuating the measurable signal requiring electrical amplification.

- Electro Cardio Gram (ECG); heart muscle acticity
- Electro Mio Gram (EMG); any muscle activity
- Electro Occulo Gram (EOG); eye movement
- Electro Encephalo Gram (EEG); brain neural activity

**Bioimpedance** measures body and tissue impedance by injecting oscillating current through electrodes and measuring the resulting voltage. The frequency response is indicative of electrical tissue composition.

- Whole Body Impedance Analysis (BIA) or Total Body Composition (TBC)
- Segmental Body Impedance (smaller regions of the body).
    - Respiratory Rate (RR)
    - Lung Composition (LC)
    - Pulmonary Edema (PE)
- Galvanic skin response (GSR), Skin Conductance Level (SCL) or Electro dermal activity (EDA)as a result of physiologic arousal

**Optical Absorption** is measured with light passing through the body and tissue at different optical wavelengths extracting optical absorption properties of tissue constituents such as hemoglobin. Variation in concentration occurs during blood pressure propagation. Background such as melanin and scattering affect these readings and can reduce signal strength. When measuring with more than two wavelenghts, additional Hemoglibin species can be detected, however most common sensor elements support two wavelenghts.

- Pulse Plethysmo Graphy (PPG); detecting the effects of pressure waves passing by the sensor, non contact heart rate and pulse propagation
- Blood Oxygenation
- $SPO_2$ Pulse Oximetery, oxygen saturation

**Temperature** is a simple measurement for increased metabolism which can be caused through viral or bacterial load as a defense mechanism to lower viral replication but also due to hyperactivity of cancer or exercise.

- External skin temperature
- Internal temperature

**Sound** is emitted as a result of mechanical activity such as heart deformation during muscle contraction, closure of valves or blood turbulence causing pressure gradients, abdominal muscle contractions, and airflow resulting in pressure wave propagation through the body.

- Heart sounds (S1, S2)
- Blood vessel sounds induced by blood pressure cuff, als know as Korotkoff sounds
- Lung sounds
- Bowel sounds

**Activity** expand here..

- Acceleration, Gyration, Mangnetic field
- Barometric Pressure
- GPS

**Respiration** .. expand here

- Air Flow
- Humidity, Temperature
- Pressure
- Light level
- $CO_2$ concentration
- Particulate matter concentration
- Presence of Volatile Organize Compounts
- Presence of Carbion Monoxide

**Cellular Structure** microscopy, expand here

**Analyte Concentrations** expand here

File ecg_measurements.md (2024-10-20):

# Electro Cardio Graphy

To be written

## Physiology

<p float="left">
    
    
</p>

Figures: https://commons.wikimedia.org/

The heart muscle creates a strong electric field that is measurable on the skin surface. Ion gradients from muscle cells sum up to a potential of ab out 3mV on the skin. To measure this signal with a modern analog to digital converter an ammplification of 100-300 is needed.

The muscle contraction of the left and right ventricle cause a sharp rise in the overall potential allowing for accurate heart rate measurements. 

Heart rate can also be measured with pelthysmography in a much safer manner. To record an ECG, electrodes need to be attached to the skin. Their contact chemistry and size reduce skin resistance to pickup the signal. These electrodes pose a safety concern because in case of an electrical failure, current can enter and exit through them more easily into the body. They are placed so that optimal signal from the heart can be measured which also results in optimal placement to inject current into the heart.  

### Electro Cardio Gram (ECG)

Heart muscle acticity

<p float="left">
     
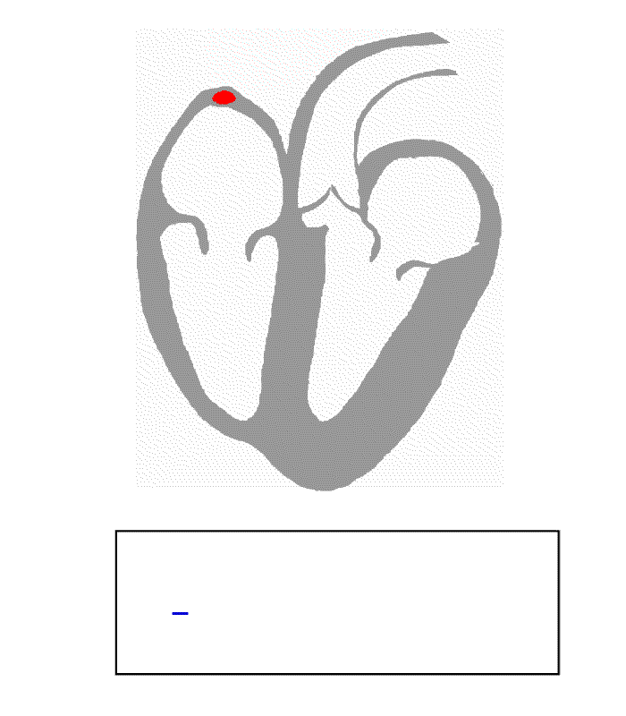
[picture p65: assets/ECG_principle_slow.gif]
    
</p>

 

Figures https://commons.wikimedia.org/

## Composition of ECG Waveform

### Cell Membrane
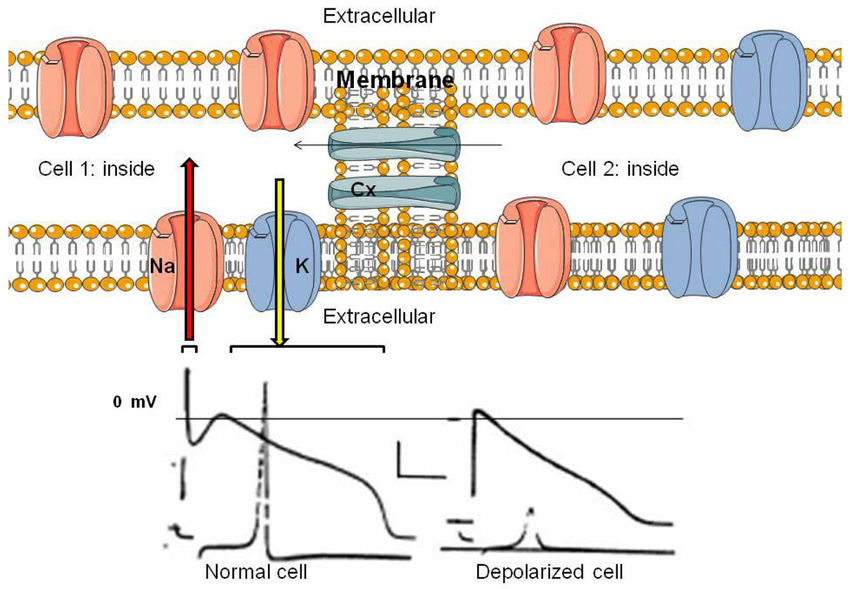
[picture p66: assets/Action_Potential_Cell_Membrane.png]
 

http://www.ncbi.nlm.nih.gov/pmc/articles/pmc2828741/

### Singe Muscle Cell Electric Potential
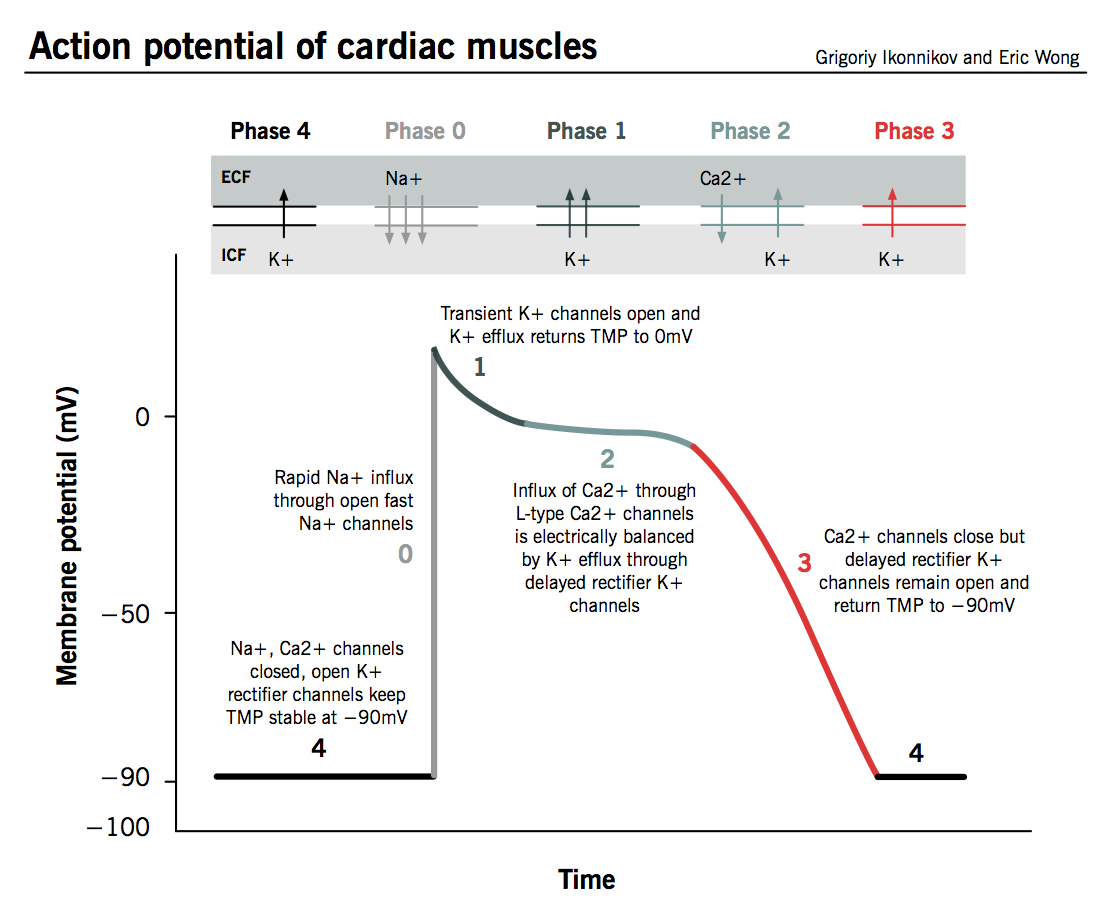
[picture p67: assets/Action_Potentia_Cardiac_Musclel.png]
 

https://www.pathophys.org/wp-content/uploads/2013/10/ActionPotential.png

### Combination of Signals
 

https://en.wikipedia.org/wiki/Cardiac_action_potential

### Triangle of Einthoven
 
https://en.wikipedia.org/wiki/Einthoven%27s_triangle

### ECG Interpretation

https://en.wikipedia.org/wiki/Atrial_fibrillation
https://en.wikipedia.org/wiki/Premature_atrial_contraction
https://en.wikipedia.org/wiki/Bundle_branch_block
https://en.wikipedia.org/wiki/Myocardial_infarction

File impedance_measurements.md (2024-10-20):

# Body Impedance

<div style="float: right; margin-left: 10px;">
Impedance
</div>

Electrical impedance is measured similarly to measuring the resistance of resistor with a multimeter. However, we also obtain reactance and the measurement is conducted with alternating current. Impedance is usually a 4-wire measurement technique where two electrodes are used to inject current into the sample and two more electrodes are used to measure the resulting potential. One can also use just two electrodes and even record a low frequency signal such as an ECG from the same electrodes as the impedance measurement. With the help of a demodulator (mixer), impedance measured at a given frequency is converted to a constant signal at 0 Hz that can be pickedup with a simple direct current measurement. The math section below explains this principle.

Intracellular and extracellular fluids contain ions that will migrate under the influence of an electric field. This is in contast to conductors and semiconductors where current is based on free electrons. Extracellular conductance is mainly due to Na+ and Cl− ions. Free proteins in the blood plasma are negatively charged and contribute also to the conductance. Extracellular and intracellular fluids are primarily resistive while cell membranes act as barriers to current flow at low frequencies acting as cpacitors. The epidermis acts more as a dielectric with some  conductive properties, while muscle tissue acts primarily as a conductor with some dielectric properties 

Thus, tissue impedance depends on intracellular and extracellular water content as well as ion concentrations, but also on fat content. Edema is an accumualtion of fluids and will change impedance. Inhalation increases the lung volume and since air is an insulator, should increase chest impedance. Total body compoisition such as muscle mass, water content and fat content affect impedance.

For Bio Impedance measurements (BIOZ), impedance is typically measured at frequencies higher than the ones representing the ECG (>1kHz). Historically an alternating current at 50kHz is used for impedance analysis on the body, however 5-100kHz or 1-1000kHz is also used for impedance spectroscopy. 

For impedance analysis, the total body but also regions of the body can be evaluated:

<div style="float: right; margin-left: 10px;">
Impedance
</div>

- **Whole Body** Impedance Analysis (BIA) or **Total Body Composition** (TBC)
- **Segmental Body** Impedance for smaller regions in the body.
  - **Respiratory Rate** (RR) model.
  - **Lung Composition** (LC) model 
  - **Pulmonary Edema** (PE) model.

For these measurements electrodes are placed on the following locations.

| Model   | Electrode 1 | Electrode 2   |
|---      |---          |---            |
| TBC     | Ankle       | Wrist         |
| RR      | Chest       | Chest         |
| LC      | Clavicle    | Ribcage       |
| Knee    | Distal Knee | Proximal Knee |
| Calf    | Distal Calf | Proximal Calf |

Besides **Impedance Analysis** there is **Impedance Spectroscopy** where impedance is measured at multiple frequencies. When changing frequencies a reactance versus resitance graph can be plotted as shown below. When conducing an impedance measurement at 0Hz reactance is zero and with increasing frequency reactance increases. At infinit freuency resistance is the lowest. When no physiological processes change impedance the values measured at different frequencies will fall onto a circle.

## Mathematical Description of Impedance Measurement

<div style="float: right; margin-left: 10px;">
Impedance
</div>

- $R$: Resistance (real part of impedance, measured in Ohms)
- $X$: Reactance (imaginary part of impedance, measured in Ohms)
- $j = \sqrt{-1}$ (the imaginary unit)

The impedance $( Z )$ is defined as comlpex number:

$$
Z = R + jX
$$

where $( Z )$ is measured in Ohms ($\Omega $).

This can also be expressed in **Euler's form** as:

$$
Z = |Z| e^{j\theta}
$$

where:
- **Magnitude**: $|Z| = \sqrt{R^2 + X^2}$
- **Phase**: $\theta = \tan^{-1}\left(\frac{X}{R}\right)$

In **rectangular form**, impedance is:

$$
Z = |Z| (\cos(\theta) + j \sin(\theta))
$$

where:
- Real part $R = |Z| \cos(\theta)$ is resistance,
- Imaginary part $X = |Z| \sin(\theta)$ is reactance.

The phase property will result in a phase delay between alternating current and the measured potential, while the magntiude determines the signal strenght of the measured potential.

## Bio Impedance Analysis

In review articles attempting to fit body composition with impedance measurements, the following common variables are used:

- $H$ Height in [cm]
- $R$ Resistance in [Ω], $R_{50}$ Resistance at 50kHz
- $X$ Reactance in [Ω]
- $Z$ Impedance $Z = R + jX$
- $W$ Weight [kg]
- $A$ Age in [years]
- $V_b$ Body Volume [liter]
- $V_e$ Extra Cellular Water (ECW) Volume in [liter]
- $V_i$ Intra Cellular Water (ICW) Volume in [liter]
- $V_t$ Total Body Water (TBW) Volume in [liter]
- $FFM$ Fat Free Mass in [kg]
- sex, with 0 for male and 1 for female tissue

For comparison with a simple resistor with a given resistivity $\rho$  [Ω cm], its resistance is $R=\rho L / A$ with A the crossection and L the length of the resistor.

### Fat Free Mass, Total Body Water, Total Body Potassium

In 1985 publication by Lukasaki [3] that was cited more than 2500 times, the authors used a 50kHz signal with 800 micro Ampere to assess the fat free body mass, total body water and total body potassium. They measured left wrist to left ankle impedance and assumed that reactance is small compared to resitstant and therefore $V = \rho L^2 / R$  They found linear relationship between their volumes and mass estimates.

$Y = {Height}^2 / R_{50}$ in units [ $cm^2 / \Omega$]

| Fat Free Mass [kg] | Total Body Water [L] | Total Body Potassium [g] |
|---            | ---              | ---                  |
| $X =  3.04 + 0.85 * Y$ | $X = 2.03 + 0.63 * Y$ | $X = -23.09 + 2.56 * Y$  |

### Water Volumes

Jaffrin et all [5] summarized several Impedance Anlysis modles in their review paper. 

#### Total Body Water

- $V_{TBW} = 0.5561 \cdot H^2/R_{50} + 0.0955 \cdot W + 1.726$
- $V_{TBW} = 0.446  \cdot H^2/R_{50} + 0.126  \cdot W + 5.82$
- $V_{TBW} = 4.65 + 0.377  \cdot H^2/R_{50} + 0.14   \cdot  W - 0.08 \cdot A + 2.9  \cdot  sex$
- $V_{TBW} = 6.53 + 0.3674 \cdot H^2/Z_{50} + 0.1753 \cdot  W - 0.11 \cdot A + 2.83 \cdot  sex$

#### Extracellular Water

- $V_{ECW} =      0.0119 \cdot H^2/X_{50} + 0.123 \cdot H^2/R_{50}        + 6.15$
- $V_{ECW} = -5.22 + 0.2 \cdot H^2/R_{50} + 0.005 / X_{50} + 0.08 \cdot W + 1.9 + 1.86 \cdot sex$

## Bio Impedance Spectroscopy

For impedance spectroscopy, measurements occur at frequencies ranging from 1 (or 5) kHz to (100 or) 1MHz.

Here, I need to expand on analysis of resitance versus reactance plot.

## Electric Equivalent Models for Bioimpedance

There are models to describe the tissue impedance and also the electrode to skin impedance asw simple electrical circuit:

| Tissue Mopdel          | Electrode Model        |
|------------------------|------------------------|
| Skin | Skin |

Ferreira et al [2] used the tissue model  to describe Total Body Composition (TBC), Respiratory Rate (RR) and Lung Composition (LC) and used the following values:

| Model   | R [Ω]    | r [Ω]  | C [nF] |
|---      |---    |---     |---   |
| TBC     | 917.5 | 665.4  | 3.42 |
| RR      |  58.5 |  25.58 | 75.7 |
| LC      |  81.5 |  22.15 | 47.7 |

Here $R$ represents the extracellular current resistance, $r$ the interacellular resistance and $C$ the capcitance introduced by cell membranes.

Paco et al [1] used the electrode model to describe measurements on the calf. The MAX30001G data sheet lists values for an electrode model that is used for a calculation where the ideal current is computed:

| Model   | R [Ω]    | r [Ω]  | C [nF] |
|---                 |---  |---   |---   |
| Electrode (Paco)   | 2k2 | 150k | 150  | 
| Electrode (30001G) | 100 |   1M |   5  |
| Calf Tissue        |  10 |  56k |  47  |

## Electric Equivalent Circuit with MAX30001G

Skin

For an example current calculation see page 36 of MAX30001G data sheet. 

I should expand the calculations here with values for the actual tissue model as in the datasheet its just a 100 Ohm resistor. Also the computation for expected noise should be included here.

## Appendix: Mathematical Derivations

### Applying Oscillating Current

When applying an alternating current to an impedance $Z$, the measured voltage is given by Ohm's law:

$$
V(t) = I(t) \cdot Z
$$

When:
- **Frequency $( f )$** is in Hz,
- $\omega = 2 \pi f$ is the angular frequency in radians per second.

We define the oscillating current as:

$$
I(t) = I_0 \sin(\omega t)
$$

or, in **Euler's form**:

$$
I(t) = \text{Re} \left\{ I_0 e^{j\omega t} \right\}
$$

The measured voltage across the impedance becomes:

1. In **Euler's form** (complex exponential form): $V(t) = I_0 \cdot |Z| \cdot e^{j(\omega t + \theta)}$

2. In **real form** (sinusoidal): $V(t) = I_0 \cdot |Z| \cdot \sin(\omega t + \theta)$

### Demodulation

When we demodulate the measured voltage by mixing it with an oscillating signal that has the same frequency but a phase offset, we multiply the measured signal with the demodulation signal:

The demodulation signal is:

   $$
   \sin(\omega t + \phi_{\text{offset}})
   $$

The demodulated Voltage becomes:

   $$
   V_{\text{demod}}(t) = I_0 \cdot |Z| \cdot \sin(\omega t + \theta) \cdot \sin(\omega t + \phi_{\text{offset}})
   $$

Using the trigonometric identity:

   $$
   \sin(\alpha) \cdot \sin(\beta) = \frac{1}{2} \left[ \cos(\alpha - \beta) - \cos(\alpha + \beta) \right]
   $$

we have:

   $$
   V_{\text{demod}}(t) = \frac{I_0 \cdot |Z|}{2} \left[ \cos((\theta - \phi_{\text{offset}})) - \cos(2\omega t + \theta + \phi_{\text{offset}}) \right]
   $$

After applying a low-pass filter, which removes the high-frequency term $( \cos(2\omega t + \theta + \phi_{\text{offset}}) )$, the demodulated voltage becomes:

$$
V_{\text{demod}} = \frac{I_0 \cdot |Z|}{2} \cos(\theta - \phi_{\text{offset}})
$$

Thus, the demodulated voltage depends on the phase difference between the Impedance's phase $( \theta )$ and the demodulation signal's phase $( \phi_{\text{offset}} )$ and  can be measured with a simple DC reading.

### Obtaining Magnitude and Phase from multiple Measurements with varying phase offsets 

At a given frequency the unknonw tissue impedance is given as magnitude $∣Z∣$ and phase $\theta$.

When measurements are conducted at several phase offsets we can determine the impedance with a least squares fit. We will record the following values:

- $\text{measurement}[i] = |Z| \cdot \cos(\theta - \phi_i)$

This can be expanded using trigonometric identities:

- $\text{measurement}[i] = |Z| [ \cos(\theta) \cos(\phi_i) + \sin(\theta) \sin(\phi_i) ]$

This equation is linear with respect to $\cos(\phi_i)$ and $\sin(\phi_i)$, allowing us to set up a linear regression problem to solve for $A$ and $B$:

- $\text{measurement}[i] = A \cos(\phi_i) + B \sin(\phi_i)$

where:

- $A = |Z| \cos(\theta), \quad B = |Z| \sin(\theta)$

Using the least squares method, the normal equations are derived from minimizing the sum of squared errors. The normal equations for this problem are:

- $A \sum \cos^2(\phi_i) + B \sum \cos(\phi_i) \sin(\phi_i) = \sum \text{measurement}[i] \cos(\phi_i)$

- $A \sum \cos(\phi_i) \sin(\phi_i) + B \sum \sin^2(\phi_i) = \sum \text{measurement}[i] \sin(\phi_i)$

To solve the full set of normal equations. we use the following steps:

1)  Calculate the sums:
- $S_{\cos\cos} = \sum \cos^2(\phi_i)$ [1]
- $S_{\sin\sin} = \sum \sin^2(\phi_i)$ [1]
- $S_{\cos\sin} = \sum \cos(\phi_i) \sin(\phi_i)$ [2]
- $S_{\text{imp}\cos} = \sum \text{measurement}[i] \cos(\phi_i)$
- $S_{\text{imp}\sin} = \sum \text{measurement}[i] \sin(\phi_i)$

2) Setup the normal equations
- $A \cdot S_{\cos\cos} + B \cdot S_{\cos\sin} = S_{\text{imp}\cos}$
- $A \cdot S_{\cos\sin} + B \cdot S_{\sin\sin} = S_{\text{imp}\sin}$

3) Compute the determinant
- $\text{determinant} = S_{\cos\cos} \cdot S_{\sin\sin} - (S_{\cos\sin})^2$ [1,2]

4) Solve for $A$ and $B$
- $A = \frac{S_{\text{imp}\cos} \cdot S_{\sin\sin} - S_{\text{imp}\sin} \cdot S_{\cos\sin}}{\text{determinant}}$
- $B = \frac{S_{\text{imp}\sin} \cdot S_{\cos\cos} - S_{\text{imp}\cos} \cdot S_{\cos\sin}}{\text{determinant}}$

5) And finally obtain magnitude and phase:
- $|Z| = \sqrt{A^2 + B^2}$
- $\theta = \arctan2(B, A)$

Two conditions should be considered resulting in the following simplifications:
- Two measurements at 0 and 90 degrees phase offset. $S_{\cos\cos}$ and $S_{\sin\sin}$ will become 1 [1] and $S_{\cos\sin}$ 0 [2]. The determinant is 1. 
- When the phase offsets are spread uniformly over the full range of offsets which is from 0 to 360 degrees the $\cos(\phi_i) \cdot \sin(\phi_i)$ term can be neglected as the sum will become zero.

## Literature

1) [Paco Bogonez-Franco et al, 2014, Problems encountered during inappropriate use of commercial bioimpedance devices in novel applications, 7 th International Workshop on Impedance Spectroscopy 2014](https://www.researchgate.net/publication/269571754_Problems_encountered_during_inappropriate_use_of_commercial_bioimpedance_devices_in_novel_applications)

2) [J Ferreira et al 2010 J. Phys.: Conf. Ser. 224 012011](https://iopscience.iop.org/article/10.1088/1742-6596/224/1/012011/pdf)

3) Assessment of fat-free mass using bioelectrical impedance measurements of the human body, H C Lukaski, P E Johnson, W W Bolonchuk, G I Lykken, PMID: 3984933 DOI: https://doi.org/10.1093/ajcn/41.4.810, 2500 citations.

4) The Theory and Fundamentals of Bioimpedance Analysis in Clinical Status Monitoring and Diagnosis of Diseases by Sami F. Khalil, Mas S. Mohktar and Fatimah Ibrahim, Sensors 2014, 14(6), 10895-10928; https://doi.org/10.3390/s140610895

5) Body fluid volumes measurements by impedance: A review of bioimpedance spectroscopy (BIS) and bioimpedance analysis (BIA) methods, Michel Y. Jaffrin, Hélène Morel, Medical Engineering & Physics
Volume 30, Issue 10 , December 2008, Pages 1257-1269 https://doi.org/10.1016/j.medengphy.2008.06.009

9) [Kassanos et al 2021, IEEE Tutorial](https://ieeexplore.ieee.org/document/9529213) or https://doi.org/10.1109/JSEN.2021.3110283

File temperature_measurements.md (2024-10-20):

# Temperature

Temperature regulation is essential for mamalian organisms as well as culture of cells and tissues. The physiologic temperature range is narrow with about $37\degree C$. Relevant environmental temperatures are between $-/+50\degree C$.

Temperature can be measured using thermoelectric effect using thermo couples. Most common is the use thermistors which change their resistance based on temperature either in negative or positive direction. The negative thermistor with room temperature resistance specified at $20\degree C$ is a common thermistor.

For medical applications the sensor is encapsulated and electrically isolated so that it can be exposed to body fluids and disinfected.

## Full bridge circuit to measure Thermistors accurately

### Wheatstone Bridge

For accurate readings, a Wheatstone bridge is needed to record the resistance of a thermistor. This is a full bridge with 4 resistors. Such bridge will be insensitive to temperature changes at the location of R1, R2 and R3 as long as they are kept close to each other.



made with https://www.circuit-diagram.org/editor

The thermistor resitance is

$R_{Thermistor} = \frac{R_3 (V_{in} R_2 - V_{diff} (R_1+R_2))}{Vin R1 + Vdiff (R_1+R_2)}$

Where $V_{diff} = V_1 - V_2$

$V_1$ and $V_2$ can be measured with a microcontroller's ADC converter. ESP ADC is of low quality and linarization and averaging in software is needed.

To implement the formula above to caculate the thermistor resistance with integer mathematics we need to use 64 bit math because resistors are 10,000 (Ohms) and $V_{in}$ is 3,300 (milli Volts) resulting in numbers larger than 32 bits.

```
int32_t R_thermistor = int32_t ( ( uint64_t(R3) * uint64_t(Vin*R2 - Vdiff*(R1+R2)) ) / uint64_t(Vin*R1 + Vdiff*(R1+R2)) );
```

### Steinhart-Hart Equation

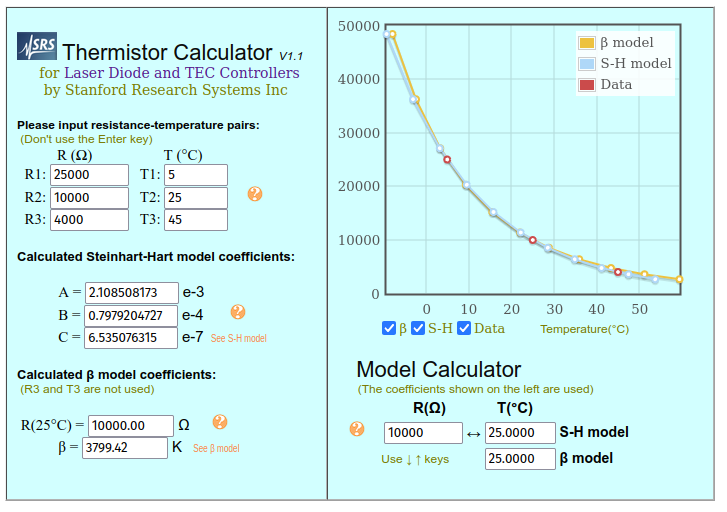
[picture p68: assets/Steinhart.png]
 

The equation provides a formula to model the resistance of the thermistor based on 3 calibration values A, B and C. These are manufacturer provided and material constants but they vary for each type of thermistor. The equation is an approximation of the semiconductors resistance model.

$\frac{1}{T} = A + B ln(R) + C (ln(R))^3$

To solve the Steinhart-Hart Equation we need to use floats as we have to compute a logarithm. We will provide integer result in $100 x  Centigrades$. On some micro controllers, log and float math takes resources. Its better to average and reduce noise on the ADC readings and then applying the floating point math to the data.

```
float lnR = log(float(R_thermistor));                // natural logarithm
float Temp = 1.0/(A + B * lnR + C * (lnR*lnR*lnR));
Temp = (Temp-273.15);                               // Kelvin to Centigrade
return int16_t(Temp*100.0);                         // convert temperature e.g. 29.12 to 2912
```

### Wheatstone Bridge measured with precision ADC

When high precision measurements are needed we can use a differential AD converter:

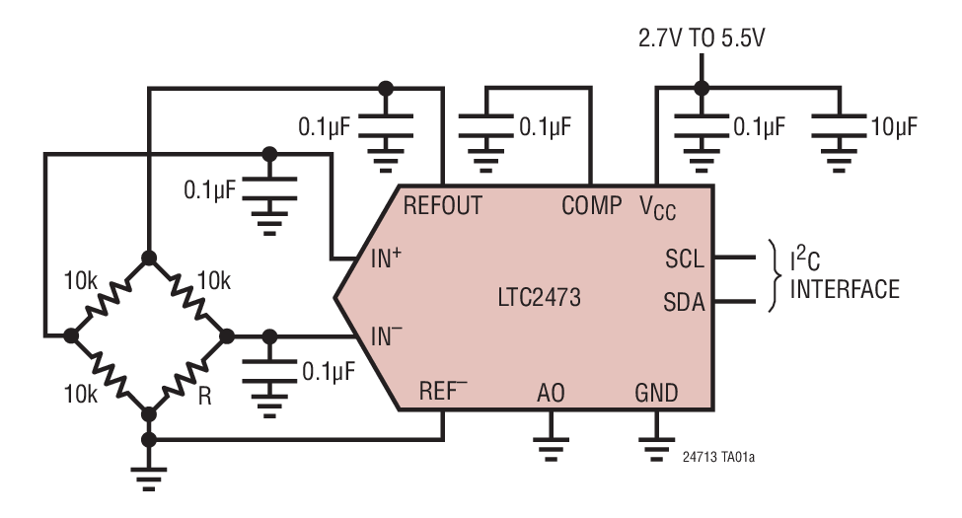
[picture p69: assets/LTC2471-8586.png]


Product [LTC2473](https://www.analog.com/en/products/ltc2473.html) has [LTC2473 data sheet](https://www.analog.com/media/en/technical-documentation/data-sheets/24713fb.pdf) and example [Arduino Software](https://github.com/analogdevicesinc/Linduino).

This converter is an inexpensive 16 bit 800 samples per second converter.

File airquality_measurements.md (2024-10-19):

# Air Quality

## Goal
To provide accurate readings for
- Particulate Matter
- CO2 concentration
- Temperature'
- Humidity
- Pressure

and to estimate concentration of
- Volatile Organic Compounds (VOC)
- Nitrogen Oxide (NOx)
- Carbon Monoxide (CO)

Values acceptable for human environment are:

| Gas | Normal    | Threshold | Excessive |  |
|---|---|---|---|---|
| CO2 | <1000ppm | 1000-5000      | > 50000 |
| rH  | 45-55 | 25-45 & 55-65  | <15 & > 80 |
| VOC | <220ppm | <660ppm | >2200ppm |
| PM2 | <13 | <55 | >150 | measured in ug/m3
| PM10 | <55 | <155 | >255 | measured in ug/m3
| $T_{body}$ | 36.4 -37.2 | <38.3 | >41.5 | 97.5 - 99F (normal)
| $T_{room}$ |  20-25| <20 or 25-30| >30 | 68 - 77F (normal)
| dP/24hrs    | | >5mbar | | pressure change

References for:
- [CO2](https://www.dhs.wisconsin.gov/chemical/carbondioxide.htm)
- [VOC 1](https://atmotube.com/air-quality-essentials/standards-for-indoor-air-quality-iaq)
- [VOC 2](https://www.advsolned.com/how-tvoc-affects-indoor-air-quality-effects-on-wellbeing-and-health/)
- [PM](https://atmotube.com/air-quality-essentials/particulate-matter-pm-levels-and-aqi)

Low humidity impacts the tear film of the eyes but also reduces virulence of airborne pathogens.

Large pressure changes can cause headaches in susceptible humans.

Cooking, heating and room occupancy affect CO2.

Presence of VOCs and Amonia is undesired.

Carbon Monoxide can lead to poisoning.

## Particulate Matter
Small particles affect the airways and can cause a variety of lung diseases. They are most commonly measured through light scattering on a steady stream of air. Scattering on particles has been studied and well described my [Gustav Mie](https://doi.org/10.1016/j.jqsrt.2009.02.022) and is a technique also used in liquid environments such as flow cytometry. The scattering phase function is affected by wavelength and particle size. Therefore to assess different particle sizes the angular distribution of a scattered collimated beam is measured. To estimate concentration to ratio between scattered and non scattered light is measured.

## CO2

Carbon dioxide can be measured electrochemically, optically and acoustically. Most inexpensive sensors use an electrochemical sensor. However for more accurate measurements a NIR absorption band of CO2 is targeted and the light transmission or acoustic wave created by pulsed light is measured.

## Pressure

Pressure is commonly recorded with a deforming membrane sealing a gas chamber. Strain gauges measure the deformation. Barometric sensors have a limited pressure range (around 1000mbar) where as fluid pressure sensors measure a larger pressure range (10atm). Altitude can be assessed to 10 centimeters where as submersion depth in water can be assessed with millimeter accuracy using these sensors.

## Humidity and Temperature
To be written

## NOx & VOC
Nitrogen Oxides in the air arise due to high temperature combustion and emissions from soil. In the atmosphere it results in acidic rain. It is used to relax smooth muscle cells to widen blood vessels(vasodilator).

Volatile Organic Compounds are human made chemicals used as solvents and refrigerants. They negatively impact the central nervous system, damage internal organs or are irritants of the airways. Under normal conditions they are not present in the air.

A variety of MEMS sensors can measure electrical equivalents of atmospheric gases through electro chemical reactions where the sensor element is heated and the presence of gases reduces its resistance. Usually there is cross sensitivity within one element with other gases.

A typical Sensirion MEMS gas sensor consumes 3mA to measure VOC and NOx. It takes 10 seconds to detect a change in VOC and about 4 mins for NOx. Sampling is typically once per second.

## Carbon Monoxide, Amonia, Nitrogen Oxides

Its difficult to find accurate and inexpensive Carbon Monoxide sensors. It is possible to calibrate less expensive sensors by measuring known levels in a test chamber. For example, there should be no Carbon Monoxide in the atmosphere indicating the sensor background level.

Carbon Monoxide is a poisonous gas because it more readily binds to hemoglobin than oxygen. 

Nitrogen Oxides and Methane should be avoided indoors.

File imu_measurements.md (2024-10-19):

# Activity Measurements

Monitoring physical activty is important for helathy as well as frail subjects. 

In healthy patients, exercise regimes are menitored with step counts.

The orientation and movement of a device can categorize wether the subject is 
standing, sitting, walking, running or laying down.

For frail patients, in addition to acticity monitoring, a fall can be detected.

# Inertial Measurement Unit Medibrick

The IMU solution consists of an Inertial Measurement Unit (IMU) as well as a precision pressure sensor 
that can measre altitude based on athmospheric pressure.

The system can serve as attitude calculator, a step counter, speed estimator, as well as a level.

# IMU

A 9-axis IMU consits of an **acceleromter**, a **gyroscope** and optinally a **mangetometer**. 
It measures orientation of gravity, rotation rate of the system and the magnetic field vector.
For each of the 3 spatial coordinates the IMU internally uses 3 sensors oriented perpendicularly to each other. 
Through sensor fusion, the systems orientation as well its residual acceleration can be calcualted even when the sensor is moving.

Since gravity is strong, orientation measurement of the device is usually accurate. 
However rotation around the gravity vector (heading) requires a compass. 
The magnetic field is often disturbed indoors through metal reinforcement in the concret and electric fields of motors. 

In order to measure gyration (rate of rotation) a gyroscope is used. 
MEMS based gyroscopes measure corriolis forces. Their sensitivity does not allow to detect earth's roation. 
Their drift will need to be compensated during runtime. Light based gyroscopes are more accurate; they measure 
a spetral shift of light in a fiberoptic ring but their cost is orders of magntiude large than MEMS devices.

To compute translation and speed, gravity subtracted acceleration needs to be caclculated.
However the integration of a signal with a strong background such as gravity subtracted acceleration leaads to run off. 
Its usually not possible to compute position throgh an integration of speed with an IMU but speed can be estimated based 
on integration of acceleration.

## MEMS

Micro-electromechanical systems (MEMS) are devices created with processes developed for integrated circuits. 
Mechanical components are edged into Silicon.

A typical MEMS structure is shown below. Itis a **Comb Capacitor** used as electrostiatic mechanical driver.
WHen an electric potential is applied the electrostatic forces from the charge on the fingers of the comb drives the capacitor appart.
If an oscuillating potential is applied the comb will resonate and and through tuning of the frequency it can be drive at its eigen freuqency. 
A similar principle can be employed to measre the structures position by measuring the capacitance. 

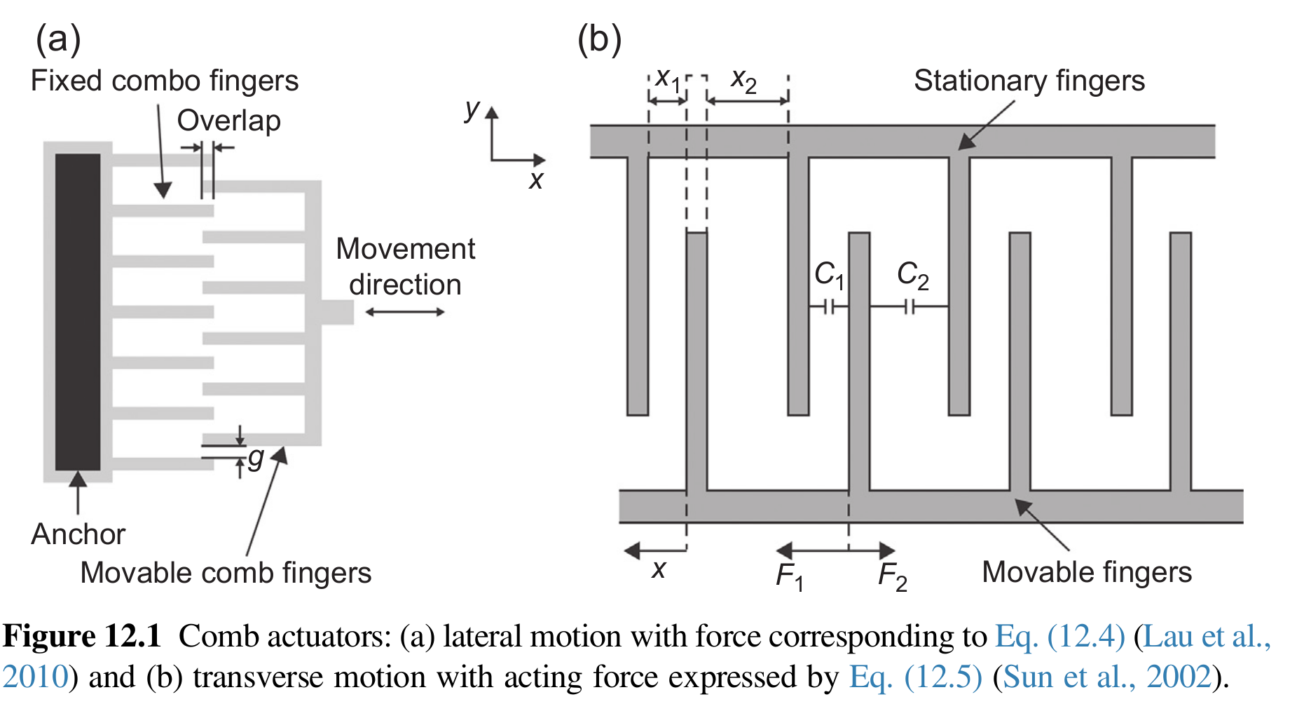
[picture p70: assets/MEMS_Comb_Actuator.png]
Comb Actuator

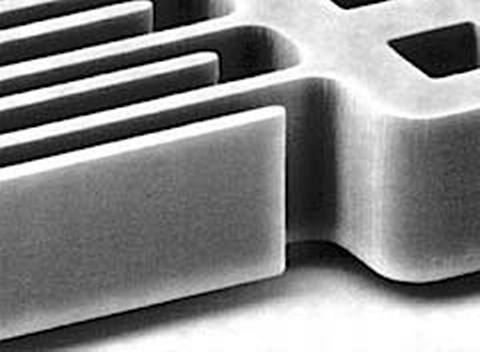
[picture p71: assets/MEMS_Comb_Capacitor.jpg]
Comb Capacitor


https://ieeexplore.ieee.org/abstract/document/6495768

### Accelerometer

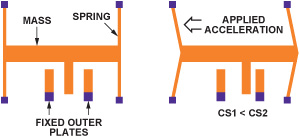
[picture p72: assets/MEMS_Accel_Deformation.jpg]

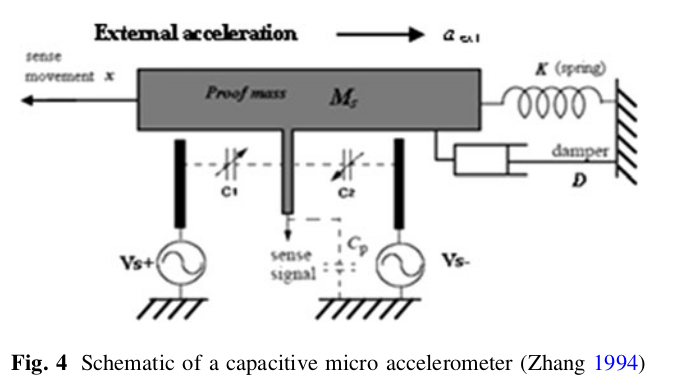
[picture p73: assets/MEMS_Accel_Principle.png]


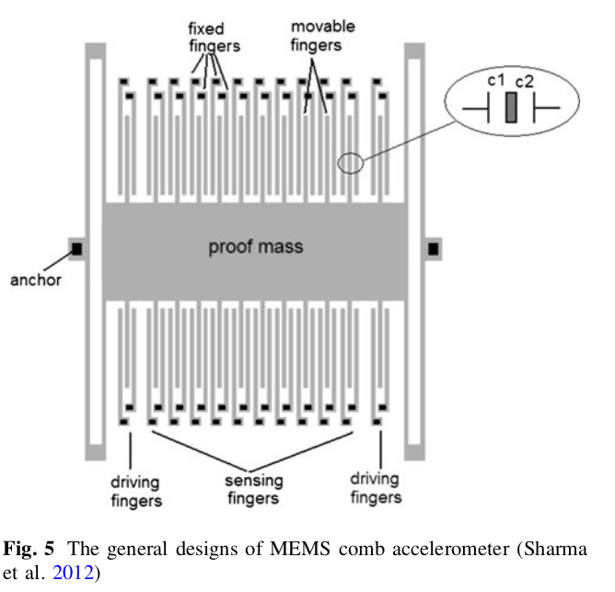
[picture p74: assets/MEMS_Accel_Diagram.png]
MEMS Accel


Buffa et al. Compact MEMS magnetometers for inertial measurement units https://doi.org/10.1007/s00542-013-1741-z

### Gyroscope

Gyro Type 1
Gyro Type 2
Gyroscope

[Shel, Type I and Type II Micromachined Vibratory Gyroscopes](https://www.researchgate.net/publication/228641584)

### Mangetometer



[Bahreyni, Behraad, Univ. of Cambridge, Sensors Journal, IEEE 7(9), 2007](https://doi.org/10.1109/JSEN.2007.902945)

### Pressure Sensor




## Fusion Algorithm

 

[Magdewick, An efficient orientation filter for inertial and inertial/magnetic sensor arrays](https://forums.parallax.com/uploads/attachments/41167/106661.pdf)

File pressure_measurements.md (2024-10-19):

# Pressure

Heart

Arterial Pressure

Venous Pressure

Wiegert Diagram

## Example pressure ranges
- systolic > 140mmHg  maximum 0.25bar
- diastolic 60-80mmHg minimum: 0.05bar
- lung 300cm H2O -170cm H2O -0.5bar .. 0.75bar

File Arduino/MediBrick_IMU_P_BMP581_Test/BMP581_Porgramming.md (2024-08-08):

# BMP 581 Programming

Use the BMP5_api from Bosch. Check examples in the BMP5_api. 
They are general and not made for Arduino IDE but show how its done.
You can update BMP5_api by copying its contents from BOSH https://github.com/boschsensortec/BMP5_SensorAPI to src/bmp5_api folder (do not copy examples)

## Sparkfun Device Driver

Summarized from exampple programs in Bosch api distribution.

### Preparation of Device Interface

- interface init
    - set dev_addr_pin / CS_pin
    - set read function to custom readRegister
    - set write function to custom writeRegister
    - set intf to SPI
    - set dev address pin to output and low. This is integrated in readRegister and writeRegister and does not need to be done here.
    - set spi (bus, speed 7.5MHz, MODE0)

### Init the Sensor
Sparkfun driver does reset first. This has issue as the reset function does not sendy dummy read first which is necessary for the sensor to switch to SPI mode.
Correct approach according to examples from Bosch api is to use init as first command. Bosch examples do not use reset function, its not clear how and when it should be used.

Init usually fails at power up check. This checks non volatile memory ready and error. Perhas writting custom content to it at first use will solve the issue.

- bmp5_init

### Configure the Sensor

From Bosch example forced read.

- set power mode BMP5_POWERMODE_STANDBY
    
- press_en = BMP5_ENABLE with bmp5_set_osr_odr

- configure iir filter
    - iir_flush_forced_en
    - set_iir_t
    - set_iir_p
    - shw_set_iir_t
    - shdw_set_iir_p
    - bmp5_set_iir_config(set_iir_cfg)
    
- configure interrupts
    - bmp5_configure_interrupt(BMP5_PULSED, BMP5_ACTIVE_HIGH, BMP5_INTR_PUSH_PULL, BMP5_INTR_ENABLE, dev)
    - int_source_select.drdy_en = BMP5_ENABLE;
    - bmp5_int_source_select(&int_source_select, dev);
                
### Finally
- get sensor data

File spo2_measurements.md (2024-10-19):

# Pulseoximetery

## Physiology

Oxygen and Glucose enable aerobic glycolysis which produces ATP. Oxygen is transported to the cells through perfusion and diffusion. Its taken up from the inhaled air and bound to hemoglobin in red blood cells. The oxygenation is usually efficient and almost all hemoglobin molecules pick up 4 oxygens in the lung's alveoli.

The Oxygen Saturation is determined by the ratio of oxy-hemoglobin to the total hemoglobin:

$HbO_2 Sat = \frac{c_{HbO_2}}{c_{Hb}+c_{HbO_2}}$ 

This is expressed as per cent.

However, when partial pressure of oxygen is low such as at high altitude or when there is obstruction of ventilation, oxygen saturation can fall below 90%. A lack of oxygen supply results in inability of muscles to exert force and cognition and analytic thinking is impaired. Unfortunately there is no biologic sensory system detecting such condition.

Luckily we can measure oxygenation of hemoglobin non-invasively because it changes its optical properties when it binds oxygen. For example in the red, oxygenated hemoglobin absorbs less then deoxygenated hemoglobin. This is inverted in the near infrared making those wavelengths ideal for a sensitive measurement approach.

<div style="text-align: left;">
    
</div>

As we are less interested in the venous oxygenation as compared to the arterial oxygenation, we need to derive a technique to extract the arterial contribution to the optical signal. This is accomplished by measuring the component changing with each heartbeat as the pressure waves extend the arteries and increase the optical path length through arterial blood while the venous blood flow does not results in vessel extension with each heart beat and its contribution the absorption remains constant.

Blood pressure in artierial vessels is illustrated over distance from the heart:

<div style="text-align: left;">
    Pressure
</div>

## Optical Properties of Hemoglobin

The color of tissue and skin can be explained with the optical properties of its main constituents. Here the main interest is Hemoglobin.

<div style="text-align: left;">
  Spectra
</div>

Absorption in the blue would be much stronger, however optical penetration is also affected by increased scattering. To maintain a strong signal on the sensor, measurements occur in the wavelength range of the "optical window" of tissue which is in the red to near infrared.

To simply detect the heart rate, measurements in the green create stronger signal fluctuation as compared to the red, however the largest differences between oxy and deoxy hemoglobin are in the red and near infrared.

**Molar attenunation coeficient** $a(\lambda)$ with units [ $\frac{1}{cm M}$ ] expresses the attenuation properties as function of concentration and pathlength. Relevant examples at two wavelengths are given below:

| Wavelength [nm] | Deoxyhemoglobin  | Oxyhemoglobin | Water [$\frac{1}{cm}$]
| -----------| --------------- | -------------| -----------------
| 660 nm (red)| 3226.56        | 319.6        | 0.0036
| 940 nm (nir)| 693.44         | 1214         | 0.29

$M = moles/Liter$

Absorbance $A = a \cdot c \cdot L$ with $c$ the concentration and $L$ the pathlength.

Absorbance is depending on wavelength $\lambda$ and the optical properties of the absorbers. Here we focus on $a_{Hb}$ and $a_{HbO_2}$ as we need to know the relative concentration of those two constituents.

Absorbance through a path length $L$ is

$A(\lambda) = \left[ a_{Hb}(\lambda) \cdot c_{Hb} + a_{HbO_2}(\lambda) \cdot c_{HbO_2} \right] \cdot L$ 

with $a$ the optical property and $c$ te concentration.

We choose two wavelengths $\lambda_1$ and $\lambda_2$ with $\lambda$ in the red (660nm) and near infrared (940nm) resulting in $A_{\lambda_1}$ and $A_{\lambda_2}$.

Assuming that the pathlength $L$ is the same for both wavelengths we can show that:

$HbO_2 Sat = \frac{\frac{A_{\lambda_1}}{A_{\lambda_2}} * a_{Hb,\lambda_2} - a_{Hb,\lambda_1} } { \frac{A_{\lambda_1}}{A_{\lambda_2}} \left[ a_{Hb,\lambda_2} - a_{HbO_2,\lambda_2}\right]  + \left[ a_{HbO_2,\lambda_1} - a_{Hb,\lambda_1}\right] }$

Light passing through a piece of tissue is attenuated with:

$\frac{I}{I_0} = 10^{-A}$

With $I_0$ the light incident to the tissue, $I$ the light leaving the tissue and $A$ being the sum of all absorbing components in the tissue such as 

$A_{skin} + A_{bone}+ A_{muscle} + A_{fat} + A_{water} + L_{venous} \cdot \left[ a_{Hb} \cdot c_{Hb_{venous}} + a_{HbO_2} \cdot c_{HbO_{2_{venous}}} \right] +  L_{aterial} \cdot \left[ a_{Hb} \cdot c_{Hb_{arterial}} + a_{HbO_2} \cdot c_{HbO_{2_{arterial}}} \right]$

Assuming that within a short time frame only $L_{arterial}$ changes one can lump all the other components into a constant:

$A = const +  L_{arterial} \cdot \left[ a_{Hb} \cdot c_{Hb_{arterial}} + a_{HbO_2} \cdot c_{HbO_{2_{arterial}}} \right]$

Figure: Illustration of PPG with actual measurement.

<p float="left">
     
    
</p>

Lets call the maximum signal $PPG_{relaxed}$ and the minimum signal $PPG_{extended}$ corresponding to diastole (relaxation of blood vessels due to decreased pressure) and systole. This signal as expected follows closely the arterial blood pressure.

$PPG_{relaxed} = I_0 \cdot 10^{-const +  L_{aterial_{relaxed}} \cdot \left[ a_{Hb} \cdot c_{Hb_{arterial}} + a_{HbO_2} \cdot c_{HbO_{2_{arterial}}} \right]}$

with $I_0$ being the initial power of the light when entering the tissue and $PPG$ when it leaves.

When forming a ratio between extended and relaxed:

$log \frac{PPG_{extended}}{PPG_{relaxed}} = -\Delta L \cdot \left[ a_{Hb} \cdot c_{Hb_{arterial}} + a_{HbO_2} \cdot c_{HbO_{2_{arterial}}} \right]$
where $\Delta L$ is the difference between $L_{extended}$ and $L_{relaxed}$

We can extract this number from our measurement and call it $R_{lambda}$

The fraction of two of those numbers at different wavelengths will eliminate $\Delta L$.

$R = \frac{R_{660}}{R_{940}} =  \frac {a_{Hb_{660}} \cdot c_{Hb_{arterial}} + a_{HbO_{2_{660}}} \cdot c_{HbO_{2_{arterial}}} }  {a_{Hb_{940}} \cdot c_{Hb_{arterial}} + a_{HbO_{2_{940}}} \cdot c_{HbO_{2_{arterial}}} } =  \frac {a_{Hb_{660}} \cdot (1-HbO_2 Sat) + a_{HbO_{2_{660}}} \cdot HbO_2 Sat }  {a_{Hb_{940}} \cdot (1-HbO_2 Sat) + a_{HbO_{2_{940}}} \cdot HbO_2 Sat } $ 

Therefore the extraction of $PPG_{relaxed}$, $PPG_{extended}$ from two measurement traces at two wavelengths as well as the optical constants of oxyhemoglobin and deoxyhemoglobin at those wavelengths can be used to solve for

$HbO_2 Sat=\frac{a_{Hb_{660}} - R a_{Hb_{940}}}{R(a_{HbO_{2_{940}}}-a_{Hb_{940}}) - (a_{HbO_{2_{660}}}-a_{Hb_{660}})}$

Recording of the signal occurs with two LEDs and a photodiode while an microcontroller will need to extract maximum and minimum intensity of the signal. 

For simplicity, ratios can be calculated without taking the log and $HbO_2 Sat$ can be estimated using lookup tables.

The above formulas show that pathlength for the two wavelengths is assumed to be the same, however this is not correct when other optical components become more relevant such as Melanin. Typically, fluctuations of the NIR signal are weaker than the ones in the red and the sensor should be operated so that maximum values are measured at both wavelengths by adjusting the LED current when switching between the LEDs.

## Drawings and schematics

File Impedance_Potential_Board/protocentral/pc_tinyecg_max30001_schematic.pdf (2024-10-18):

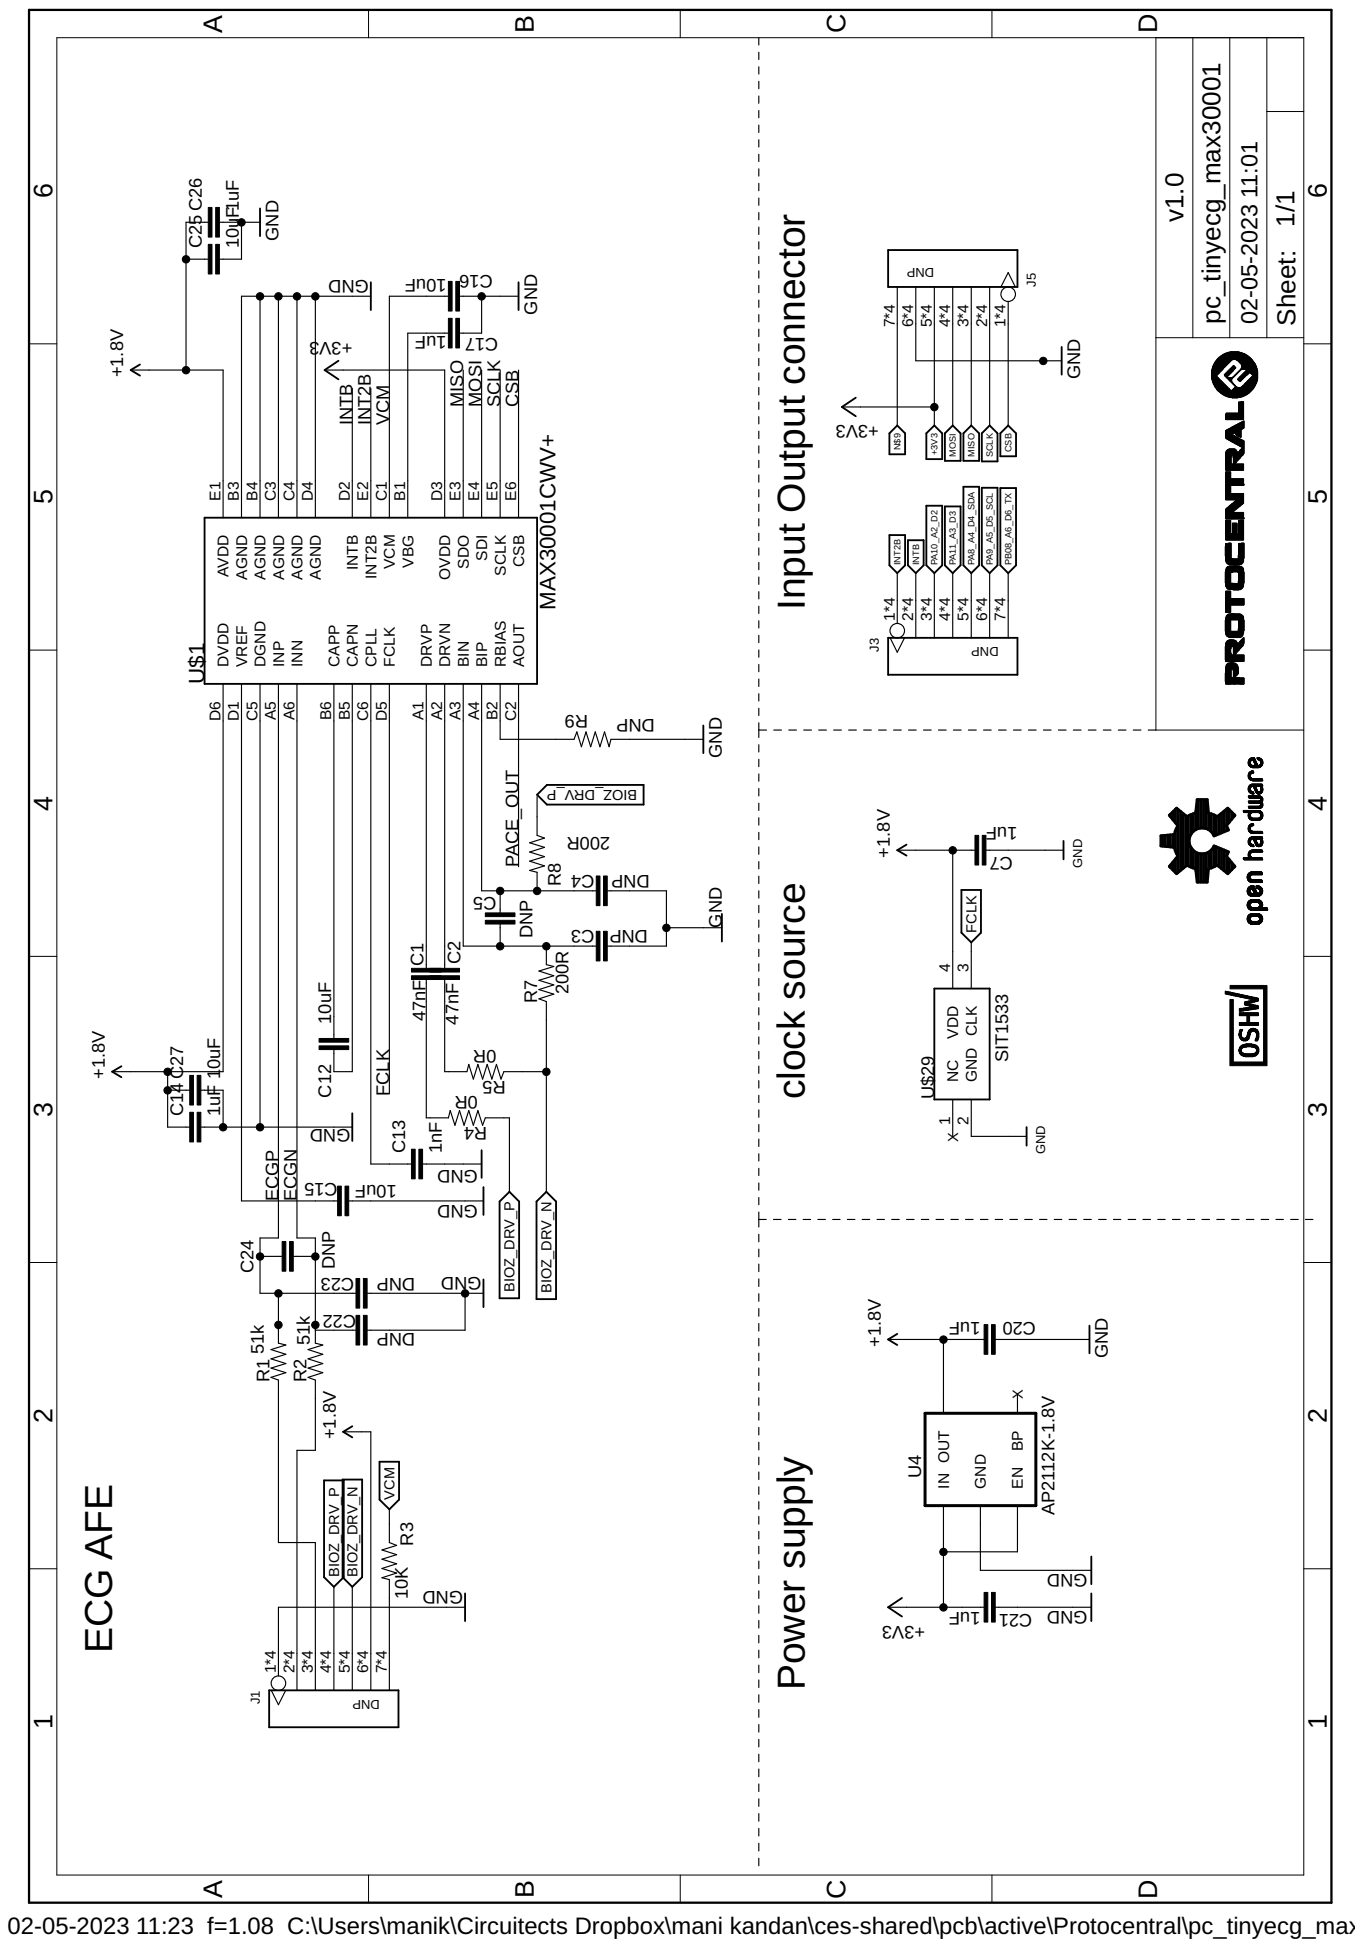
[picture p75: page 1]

02-05-2023 11:23 f=1.08 C:\Users\manik\Circuitects Dropbox\mani kandan\ces-shared\pcb\active\Protocentral\pc_tinyecg_max30001\pc_tinyecg_max30001.sch (Sheet: 1/1)

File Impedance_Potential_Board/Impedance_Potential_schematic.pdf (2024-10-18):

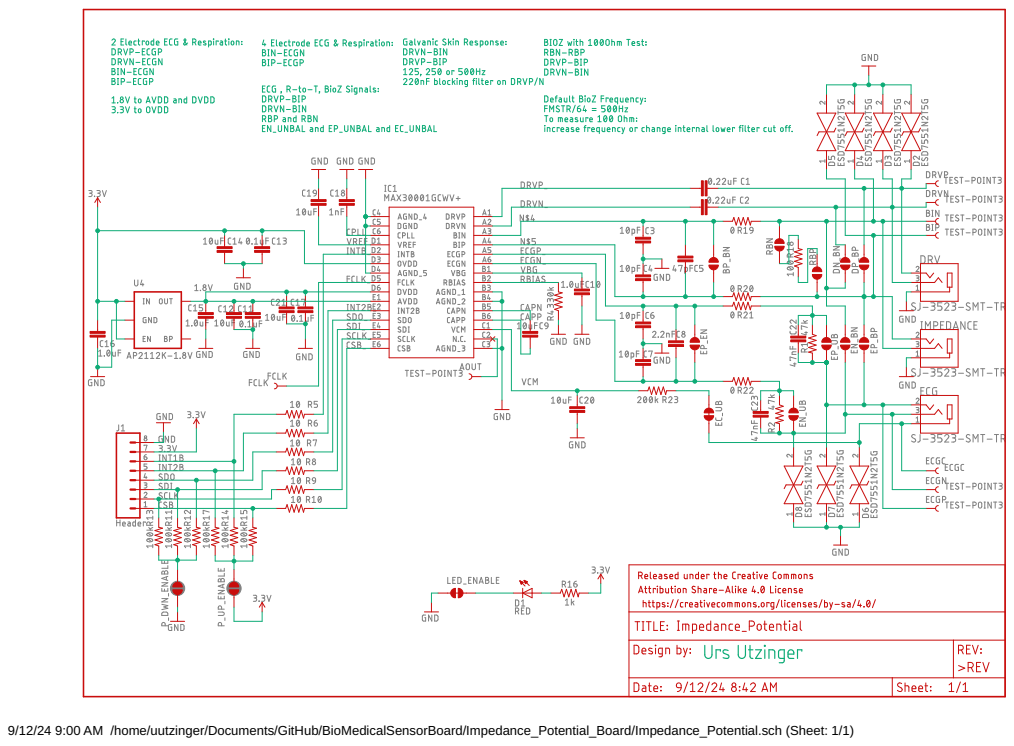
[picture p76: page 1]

9/12/24 9:00 AM /home/uutzinger/Documents/GitHub/BioMedicalSensorBoard/Impedance_Potential_Board/Impedance_Potential.sch (Sheet: 1/1)

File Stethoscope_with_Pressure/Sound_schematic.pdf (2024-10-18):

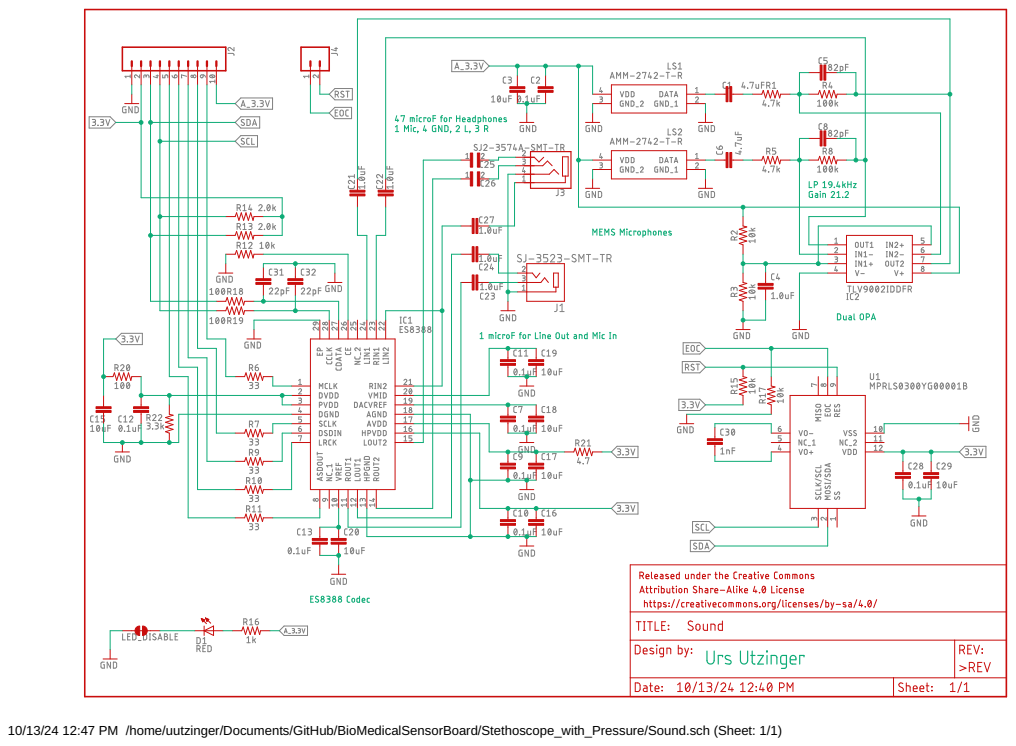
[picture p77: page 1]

10/13/24 12:47 PM /home/uutzinger/Documents/GitHub/BioMedicalSensorBoard/Stethoscope_with_Pressure/Sound.sch (Sheet: 1/1)

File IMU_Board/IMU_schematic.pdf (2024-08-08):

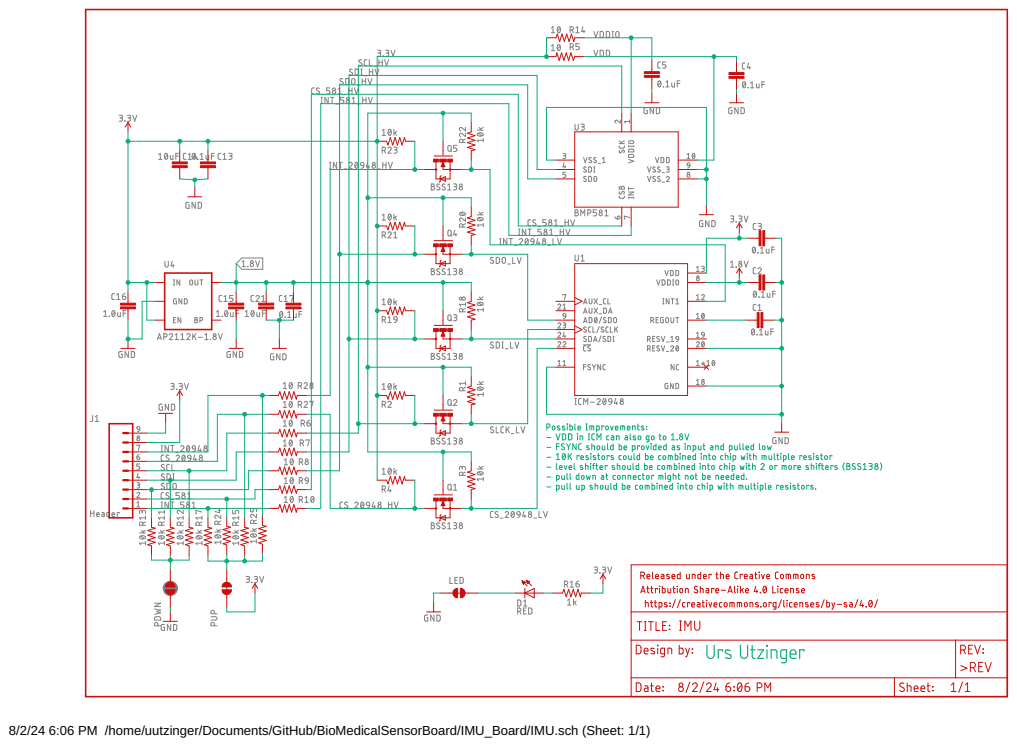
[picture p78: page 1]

8/2/24 6:06 PM /home/uutzinger/Documents/GitHub/BioMedicalSensorBoard/IMU_Board/IMU.sch (Sheet: 1/1)

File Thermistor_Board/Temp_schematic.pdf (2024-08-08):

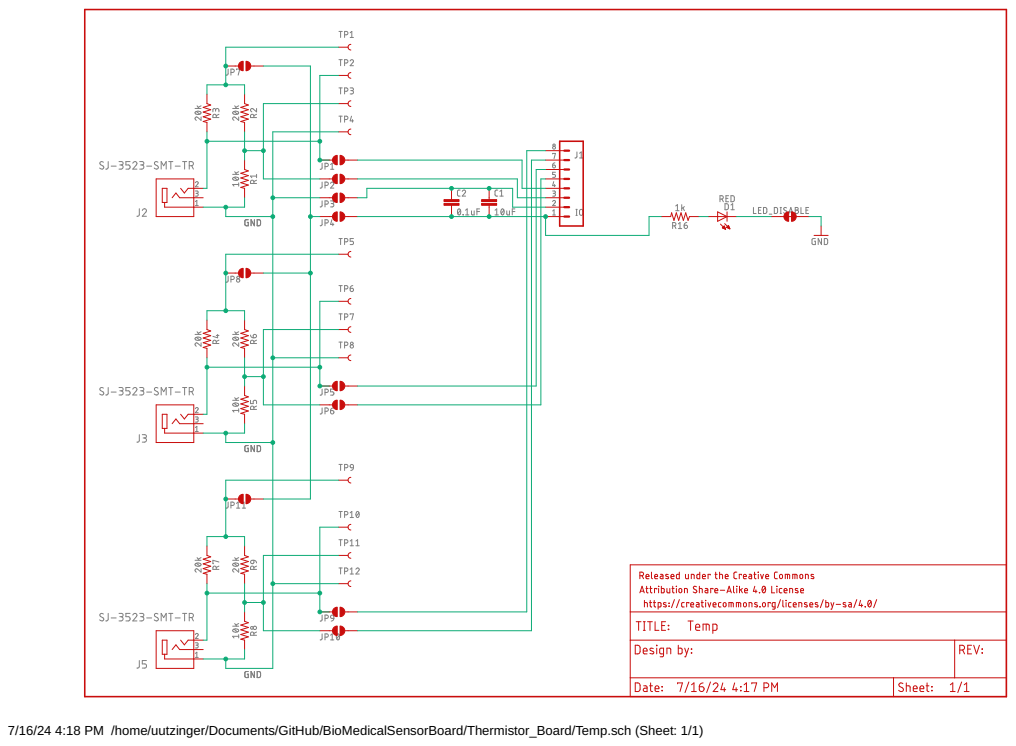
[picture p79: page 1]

7/16/24 4:18 PM /home/uutzinger/Documents/GitHub/BioMedicalSensorBoard/Thermistor_Board/Temp.sch (Sheet: 1/1)

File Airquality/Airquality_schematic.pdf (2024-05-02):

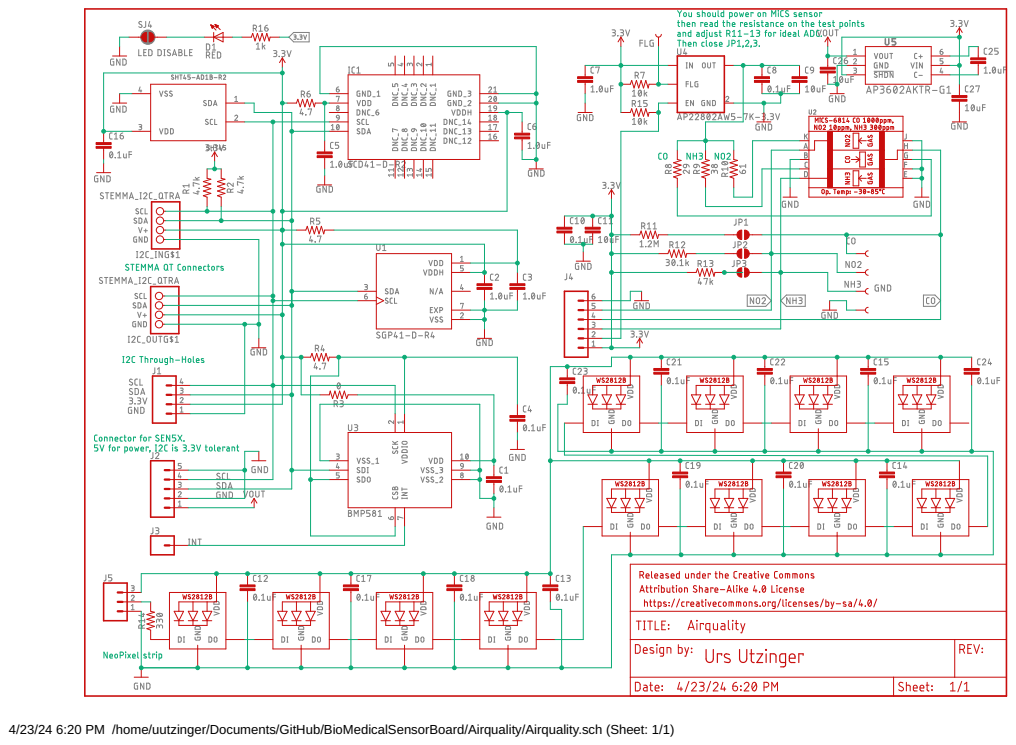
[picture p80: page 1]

4/23/24 6:20 PM /home/uutzinger/Documents/GitHub/BioMedicalSensorBoard/Airquality/Airquality.sch (Sheet: 1/1)

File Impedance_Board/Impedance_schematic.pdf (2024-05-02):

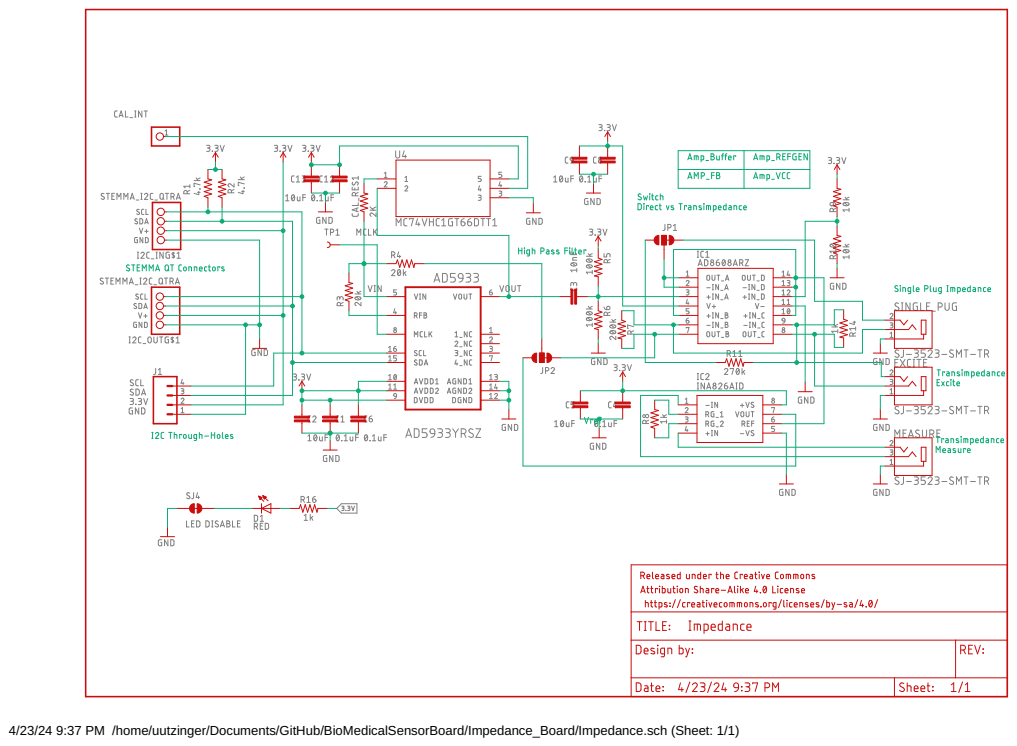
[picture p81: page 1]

4/23/24 9:37 PM /home/uutzinger/Documents/GitHub/BioMedicalSensorBoard/Impedance_Board/Impedance.sch (Sheet: 1/1)

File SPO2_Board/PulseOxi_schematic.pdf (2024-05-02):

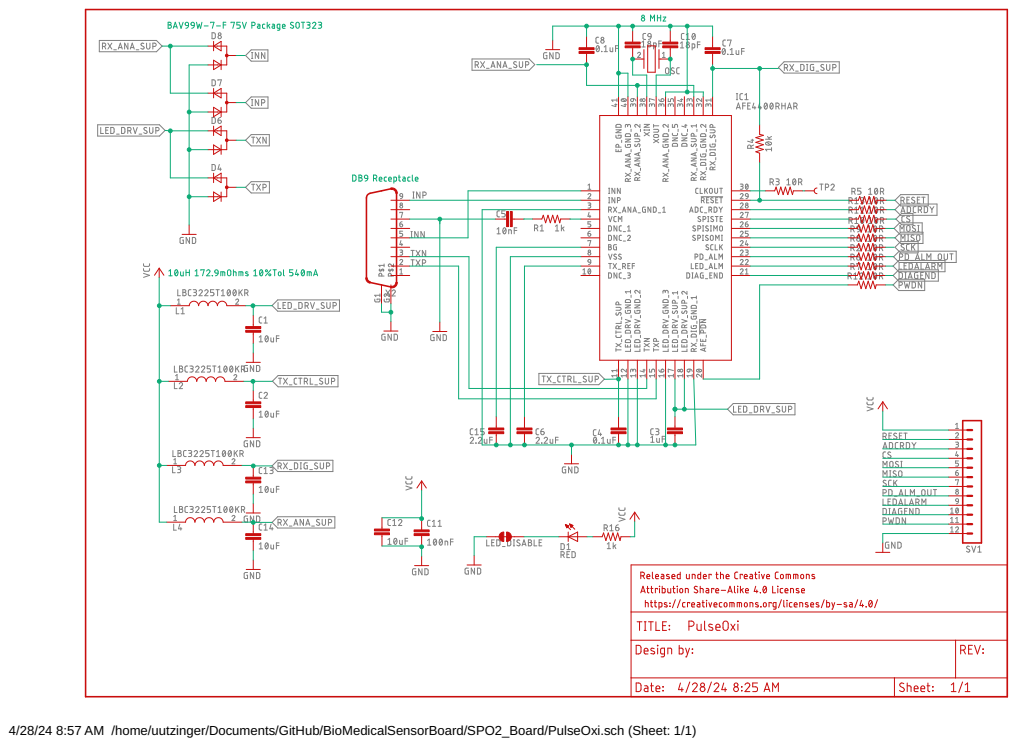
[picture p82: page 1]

4/28/24 8:57 AM /home/uutzinger/Documents/GitHub/BioMedicalSensorBoard/SPO2_Board/PulseOxi.sch (Sheet: 1/1)

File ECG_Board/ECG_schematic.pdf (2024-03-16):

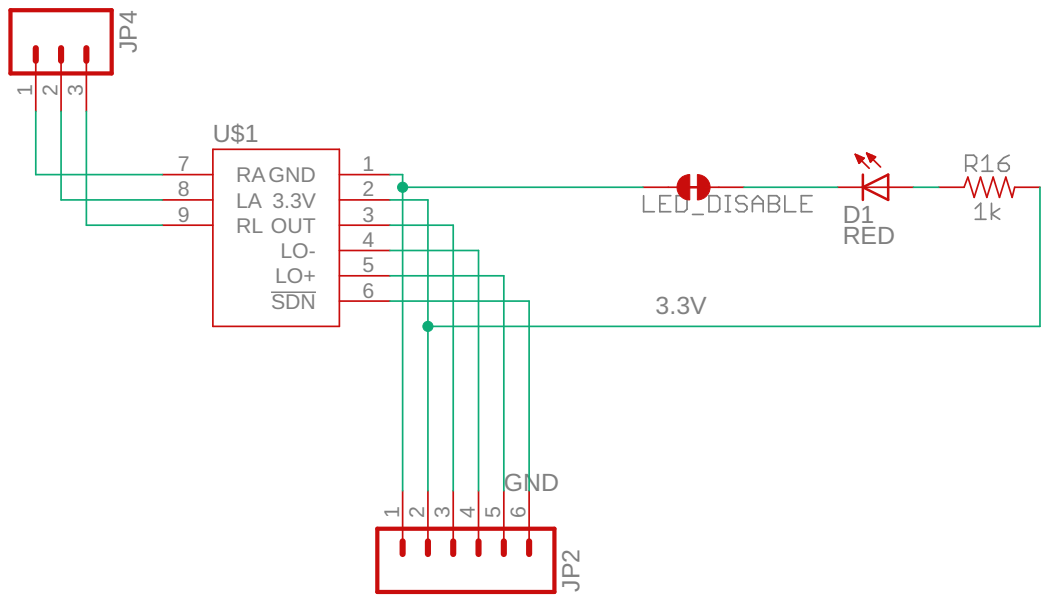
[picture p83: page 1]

5 SDN

Released under the Creative Commons Attribution Share-Alike 4.0 License

https://creativecommons.org/licenses/by-sa/4.0/

3/16/2024 12:02 PM C:\Users\uutzi\Documents\GitHub\Projects Playground\BioMedicalSensorBoard\ECG_Board\ECG 7 by 7.sch (Sheet: 1/1)

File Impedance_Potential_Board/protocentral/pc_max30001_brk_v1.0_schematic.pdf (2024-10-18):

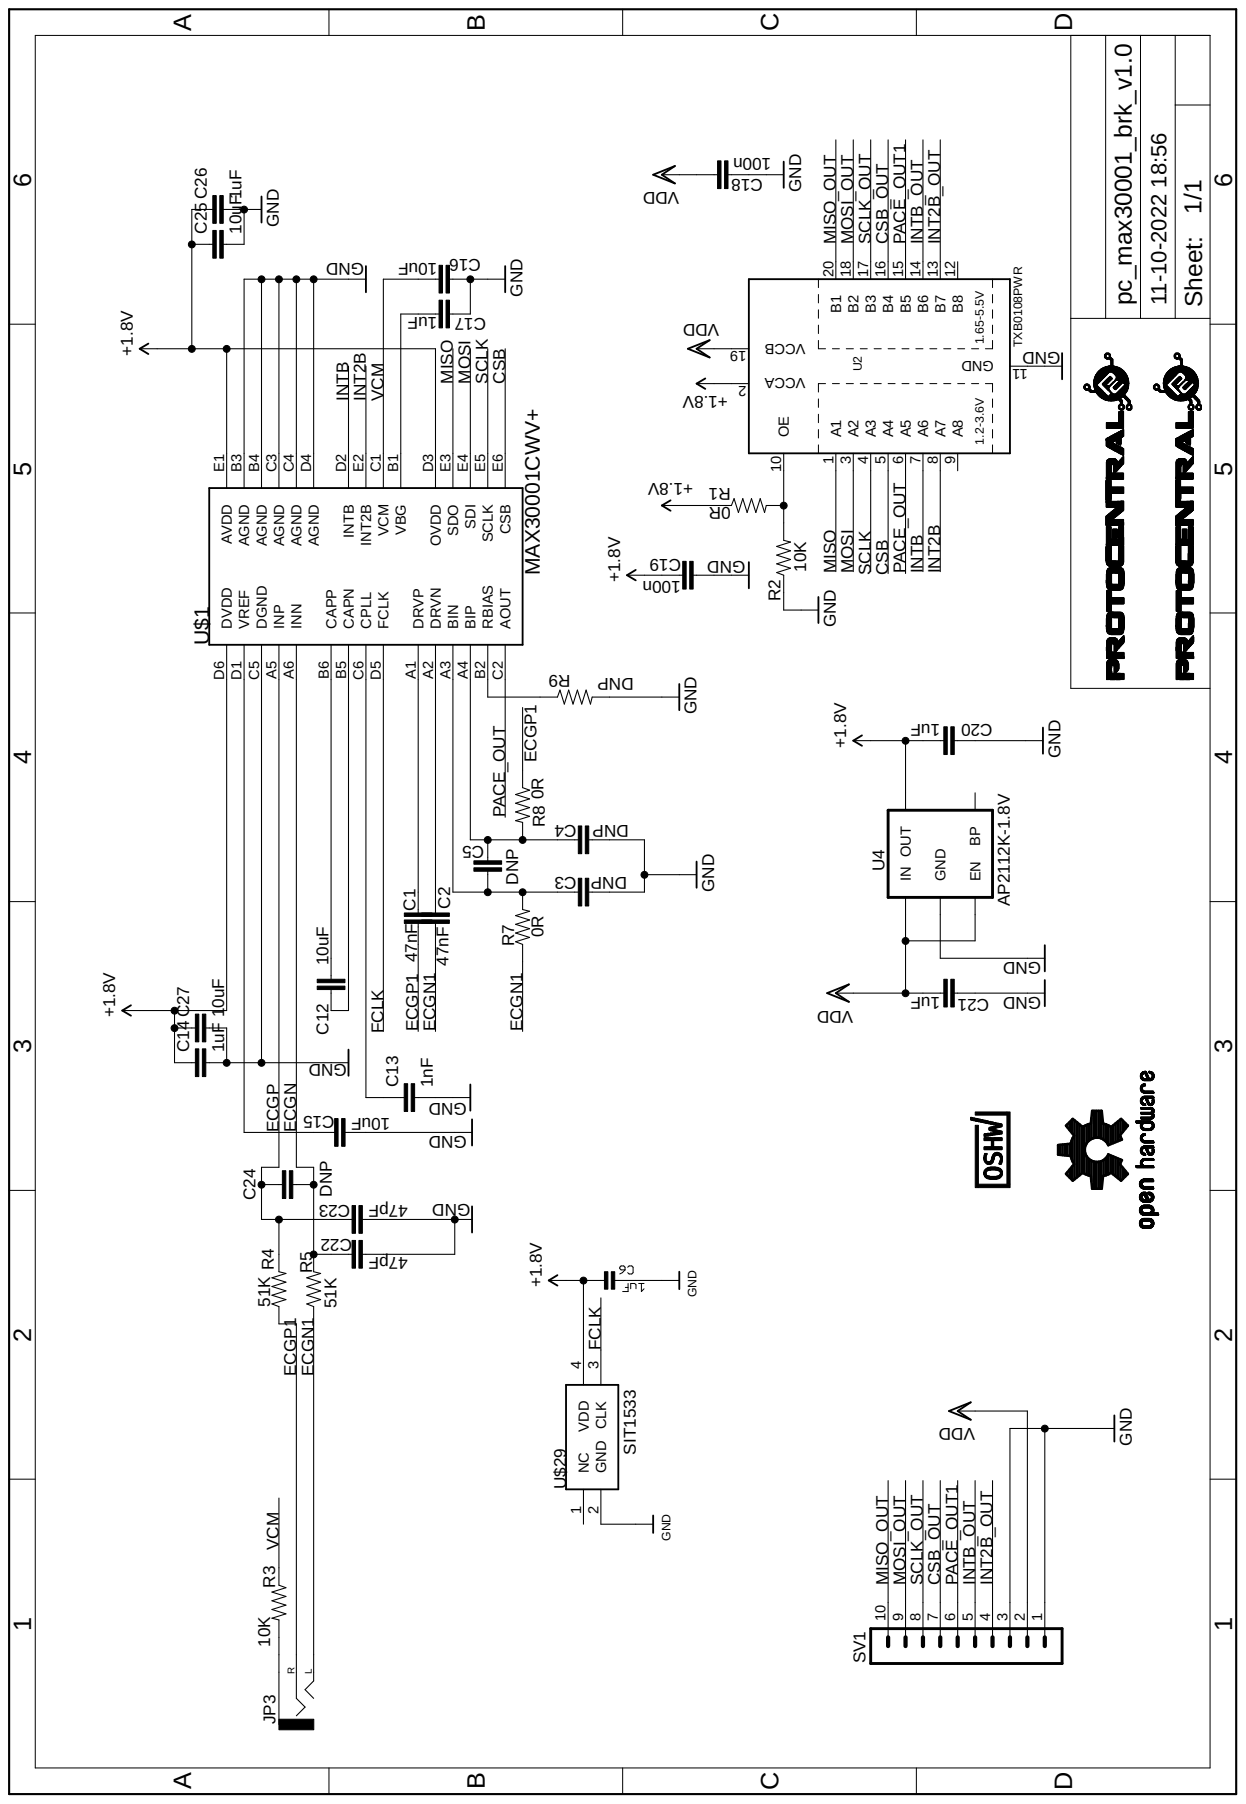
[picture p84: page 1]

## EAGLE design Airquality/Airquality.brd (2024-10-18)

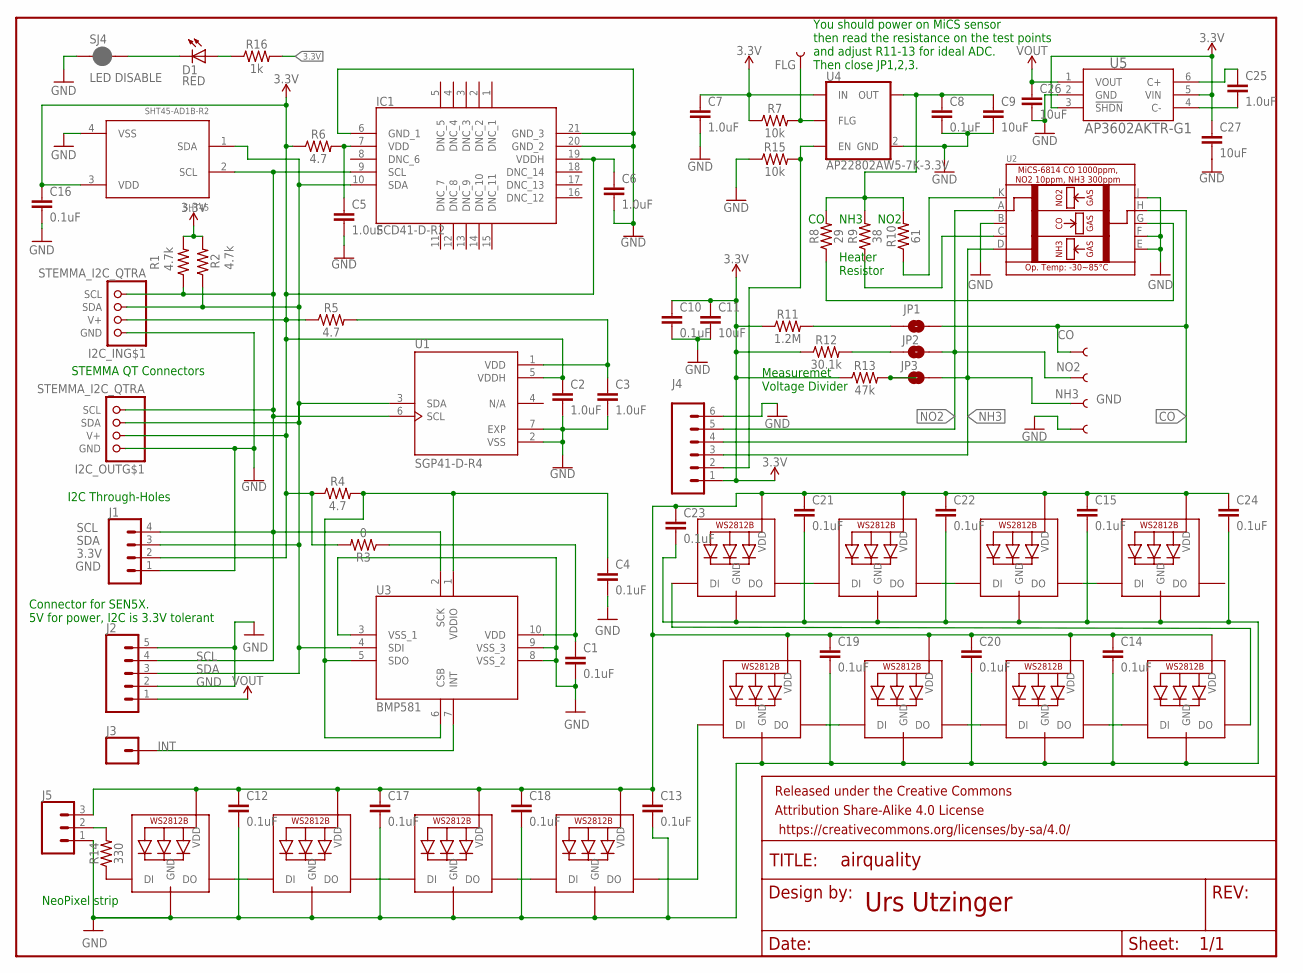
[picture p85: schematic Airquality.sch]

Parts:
C1, C4, C8, C10, C16: 0.1uF; 0603
C2, C3, C5, C6, C7: 1.0uF; 0603
C9, C11, C26, C27: 10uF; 0603
C12, C13, C14, C15, C17, C18, C19, C20, C21, C22, C23, C24: 0.1uF; 0402
C25: 1.0uF; 0402
CO: TEST-POINT3X4; PAD.03X.04
D1: RED; LED-0603
FLG: TEST-POINT3X4; PAD.03X.04
FRAME1: FRAME-LETTERNO_PACKAGE; DUMMY
GND: TEST-POINT3X4; PAD.03X.04
I2C_IN, I2C_OUT: STEMMA_I2C_QTRA; JST_SH4_RA
IC1: SCD41-D-R2; SCD41DR2
J1: CONN_04; 1X04
J2: CONN_05; 1X05
J3: CONN_01; 1X01
J4: CONN_06SILK_FEMALE_PTH; 1X06
J5: CONN_03; 1X03
JP1, JP2, JP3: JUMPER-SMT_2_NO_SILK; SMT-JUMPER_2_NO_SILK
LED0, LED1, LED2, LED3, LED4, LED5, LED6, LED7, LED8, LED9, LED10, LED11: WS2812B_2020
NH3: TEST-POINT3X4; PAD.03X.04
NO2: TEST-POINT3X4; PAD.03X.04
R1, R2: 4.7k; 0603
R3: 0; 0603
R4, R5, R6: 4.7; 0603
R7, R15: 10k; 0603
R8: 29; 0603
R9: 38; 0603
R10: 61; 0603
R11: 1.2M; 0603
R12: 30.1k; 0603
R13: 47k; 0603
R14: 330; 0603
R16: 1k; 0603
SHT45: SHT45-AD1B-R2; SHT4X
SJ4: LED DISABLE; SMT-JUMPER_2_NC_PASTE_SILK
U1: SGP41-D-R4; XDCR_SGP41-D-R4
U2: MICROBUILDER_MICS-5524
U3: BMP581
U4: AP22802AW5-7K-3.3V; SOT25
U5: AP3602AKTR-G1; SOT95P280X125-6N

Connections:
3.3V: C2.1, C6.1, C7.1, C10.1, C11.1, C16.1, C27.1, I2C_IN.2 (V+), I2C_OUT.2 (V+), IC1.19 (VDDH), J1.2, J4.1, R1.2, R2.2, R3.2, R4.1, R5.1, R6.1, R7.1, R11.1, R12.1, R13.1, R16.2, SHT45.3 (VDD), U1.5 (VDDH), U4.5 (IN), U5.3 (!SHDN), U5.5 (VIN)
CO: CO.P$1, J4.4, JP1.2, U2.H
GND: C1.2, C2.2, C3.2, C4.2, C5.2, C6.2, C7.2, C8.2, C9.2, C10.2, C11.2, C12.2, C13.2, C14.2, C15.2, C16.2, C17.2, C18.2, C19.2, C20.2, C21.2, C22.2, C23.2, C24.2, C26.2, C27.2, GND.P$1, I2C_IN.1 (GND), I2C_OUT.1 (GND), IC1.6 (GND_1), IC1.20 (GND_2), IC1.21 (GND_3), J1.1, J2.2, J2.5, J4.6, J5.1, LED0.2 (GND), LED1.2 (GND), LED2.2 (GND), LED3.2 (GND), LED4.2 (GND), LED5.2 (GND), LED6.2 (GND), LED7.2 (GND), LED8.2 (GND), LED9.2 (GND), LED10.2 (GND), LED11.2 (GND), R15.1, SHT45.4 (VSS), SJ4.1, U1.2 (VSS), U1.7 (EXP), U2.B, U2.E, U2.F, U2.J, U3.3 (VSS_1), U3.8 (VSS_2), U3.9 (VSS_3), U4.2 (GND), U5.2 (GND)
INT: J3.1, U3.7 (INT)
unnamed: C4.1, R4.2, U3.1 (VDDIO), U3.5 (SDO), U3.6 (CSB)
unnamed: C1.1, R3.1, U3.10 (VDD)
unnamed: FLG.P$1, R7.2, U4.3 (FLG)
unnamed: C3.1, R5.2, U1.1 (VDD)
unnamed: C5.1, IC1.7 (VDD), R6.2
unnamed: LED0.1 (DO), LED1.3 (DI)
unnamed: C8.1, C9.1, R8.2, R9.2, R10.2, U4.1 (OUT)
unnamed: R10.1, U2.K
unnamed: JP1.1, R11.2
unnamed: R9.1, U2.C
unnamed: JP2.1, R12.2
unnamed: R8.1, U2.G
unnamed: JP3.1, R13.2
unnamed: C25.1, U5.6 (C+)
unnamed: LED1.1 (DO), LED2.3 (DI)
unnamed: LED2.1 (DO), LED3.3 (DI)
unnamed: LED4.1 (DO), LED5.3 (DI)
unnamed: LED5.1 (DO), LED6.3 (DI)
unnamed: LED6.1 (DO), LED7.3 (DI)
unnamed: LED3.1 (DO), LED4.3 (DI)
unnamed: J5.2, R14.2
unnamed: LED0.3 (DI), R14.1
unnamed: LED7.1 (DO), LED8.3 (DI)
unnamed: LED10.1 (DO), LED11.3 (DI)
unnamed: D1.A, R16.1
unnamed: LED9.1 (DO), LED10.3 (DI)
unnamed: D1.C, SJ4.2
unnamed: LED8.1 (DO), LED9.3 (DI)
unnamed: C25.2, U5.4 (C-)
unnamed: C12.1, C13.1, C14.1, C15.1, C17.1, C18.1, C19.1, C20.1, C21.1, C22.1, C23.1, C24.1, J5.3, LED0.4 (VDD), LED1.4 (VDD), LED2.4 (VDD), LED3.4 (VDD), LED4.4 (VDD), LED5.4 (VDD), LED6.4 (VDD), LED7.4 (VDD), LED8.4 (VDD), LED9.4 (VDD), LED10.4 (VDD), LED11.4 (VDD)
unnamed: J4.2, R15.2, U4.4 (EN)
NH3: J4.3, JP3.2, NH3.P$1, U2.D
NO2: J4.5, JP2.2, NO2.P$1, U2.A
SCL: I2C_IN.4 (SCL), I2C_OUT.4 (SCL), IC1.9 (SCL), J1.4, J2.4, R1.1, SHT45.2 (SCL), U1.6 (SCL), U3.2 (SCK)
SDA: I2C_IN.3 (SDA), I2C_OUT.3 (SDA), IC1.10 (SDA), J1.3, J2.3, R2.1, SHT45.1 (SDA), U1.3 (SDA), U3.4 (SDI)
VOUT: C26.1, J2.1, U5.1 (VOUT)

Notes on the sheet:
STEMMA QT Connectors
I2C Through-Holes
Urs Utzinger
You should power on MiCS sensor then read the resistance on the test points and adjust R11-13 for ideal ADC. Then close JP1,2,3.
Connector for SEN5X. 5V for power, I2C is 3.3V tolerant
NeoPixel strip
NH3
NO2
Measuremet Voltage Divider
Heater Resistor

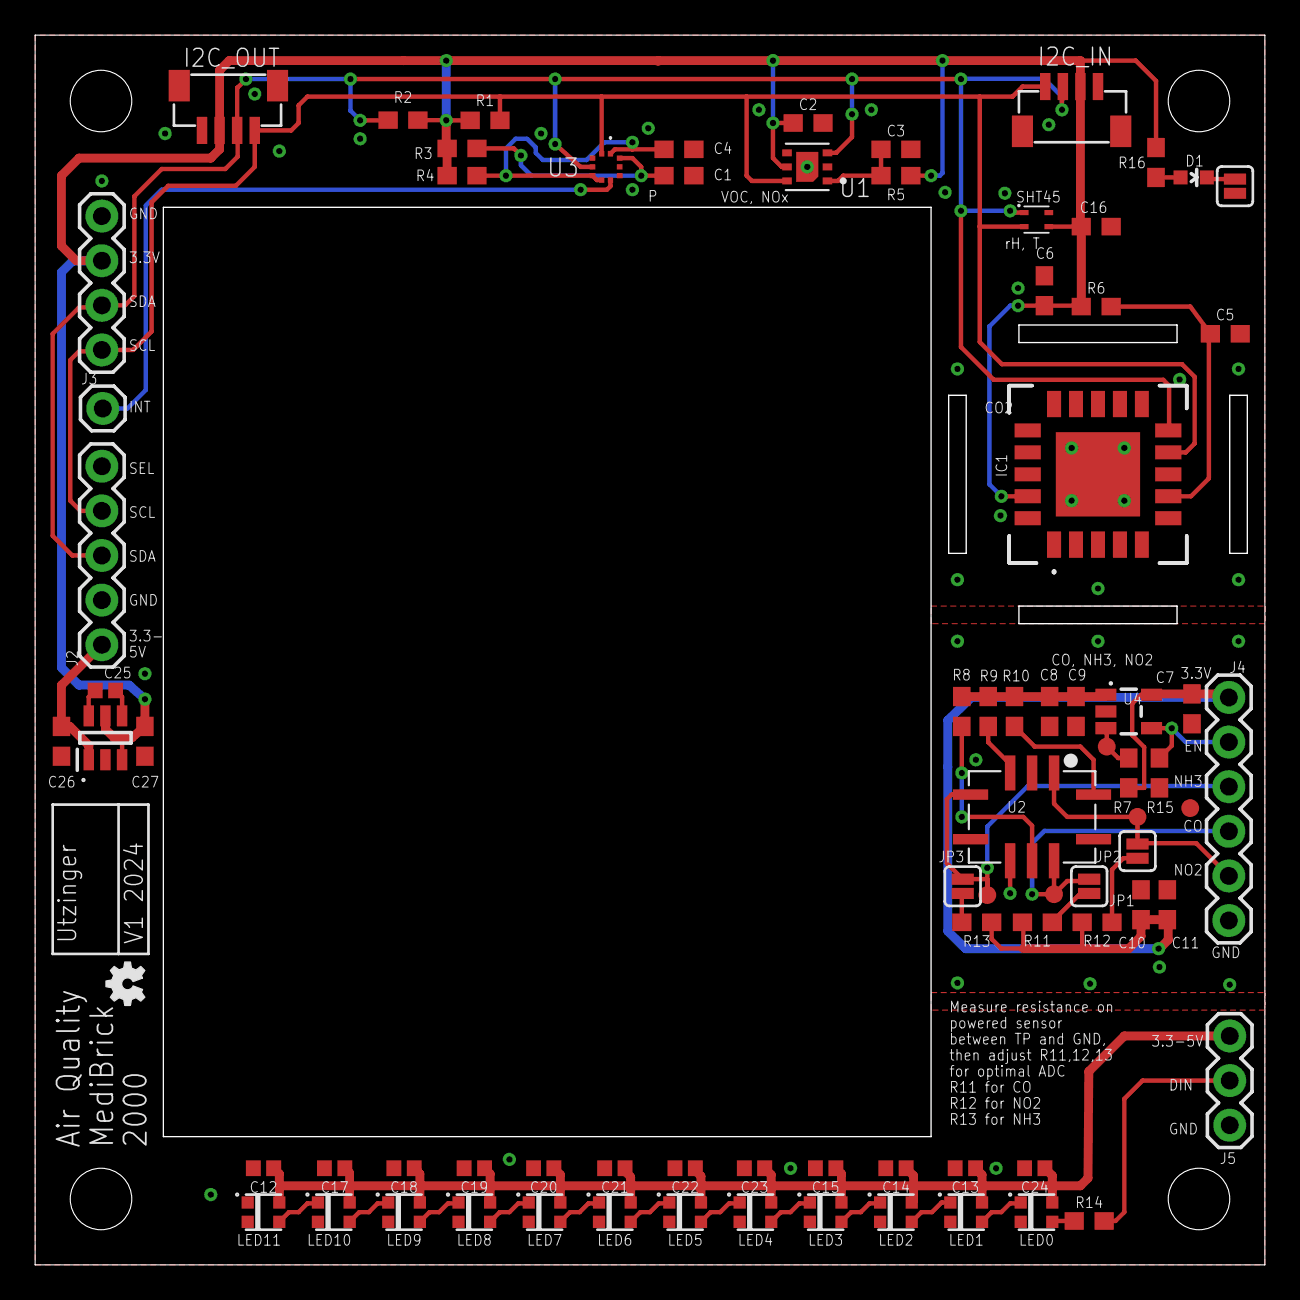
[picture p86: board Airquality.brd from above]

Board: 2 copper layers, 70.0 x 70.0 mm, 81 parts (0 on the bottom side), 40 nets.

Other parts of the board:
U$2: OSHW-LOGO-MINI

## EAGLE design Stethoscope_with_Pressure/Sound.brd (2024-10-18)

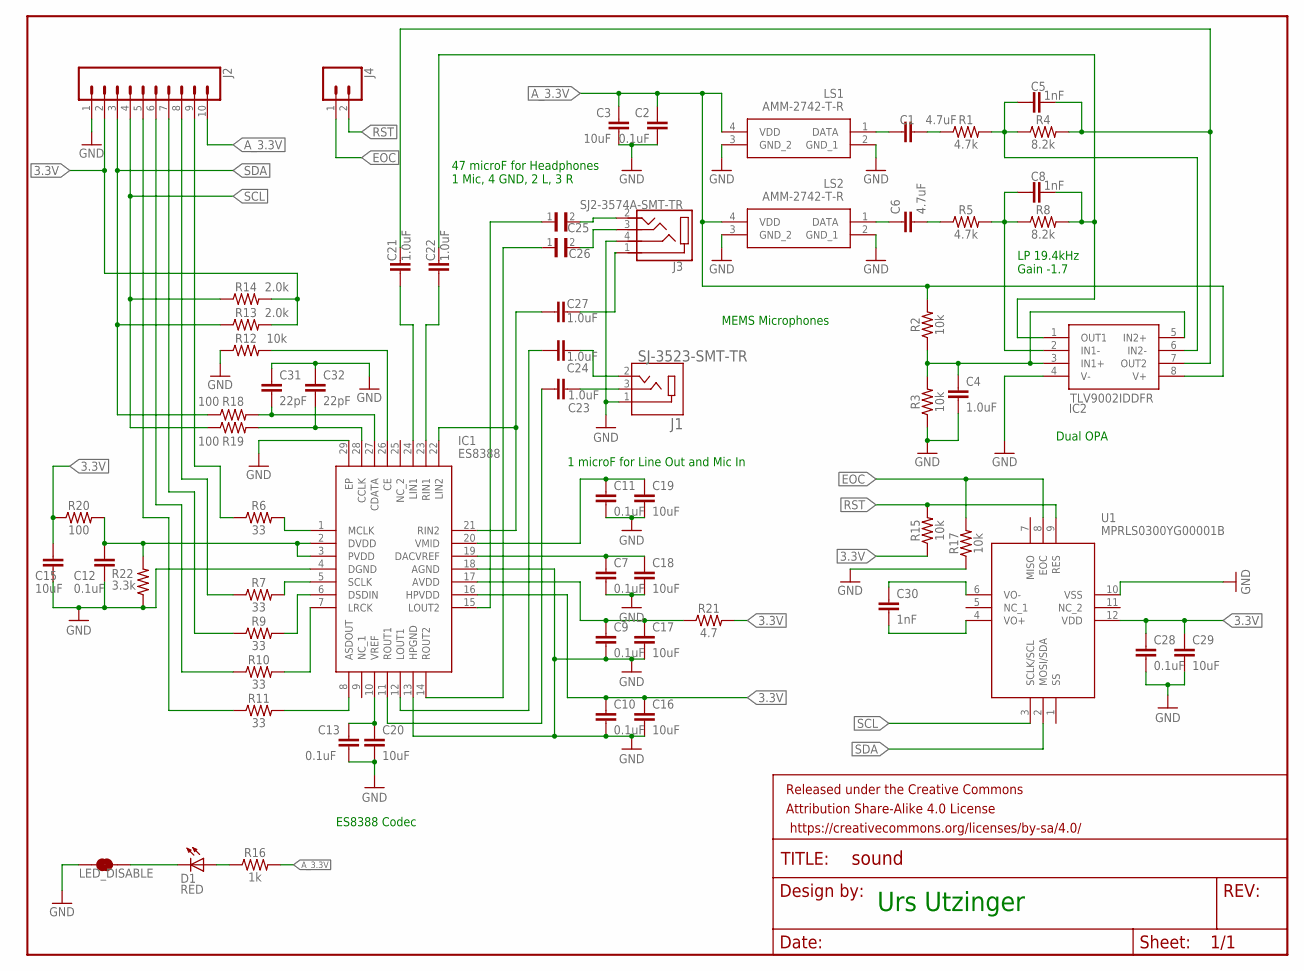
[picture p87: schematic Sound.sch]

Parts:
C1, C6: 4.7uF; 0603
C2, C7, C9, C10, C11, C12, C13, C28: 0.1uF; 0603
C3, C15, C16, C17, C18, C19, C20, C29: 10uF; 0603
C4, C21, C22, C23, C24, C27: 1.0uF; 0603
C5, C8, C30: 1nF; 0603
C25, C26: GRM188R60J476ME15D; CAPC1608X100N
C31, C32: 22pF; 0603
D1: RED; LED-0603
FRAME1: FRAME-LETTERNO_PACKAGE; DUMMY
IC1: ES8388; QFN45P400X400X90-29N
IC2: TLV9002IDDFR; SOT65P280X110-8N
J1: SJ-3523-SMT-TR; CUI_SJ-3523-SMT-TR
J2: CONN_10"; 1X10
J3: SJ2-3574A-SMT-TR; CUI_SJ2-3574A-SMT-TR
J4: CONN_02; 1X02
LED_DISABLE: JUMPER-SMT_2_NC_TRACE_SILK; SMT-JUMPER_2_NC_TRACE_SILK
LS1, LS2: AMM-2742-T-R; AMM2742TR
R1, R5: 4.7k; 0603
R2, R3, R12, R15, R17: 10k; 0603
R4, R8: 8.2k; 0603
R6, R7, R9, R10, R11: 33; 0603
R13, R14: 2.0k; 0603
R16: 1k; 0603
R18, R19, R20: 100; 0603
R21: 4.7; 0603
R22: 3.3k; 0603
U1: MPRLS0300YG00001B

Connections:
3.3V: C10.1, C15.1, C16.1, C28.1, C29.1, IC1.16 (HPVDD), J2.2, R13.2, R14.2, R15.1, R20.1, R21.2, U1.12 (VDD)
A_3.3V: C2.1, C3.1, IC2.8 (V+), J2.10, LS1.4 (VDD), LS2.4 (VDD), R2.2, R16.2
DIN: J2.7, R9.1
DOUT: J2.5, R11.1
EOC: J4.1, R17.2, U1.8 (EOC)
GND: C2.2, C3.2, C4.2, C7.2, C9.2, C10.2, C11.2, C12.2, C13.2, C15.2, C16.2, C17.2, C18.2, C19.2, C20.2, C28.2, C29.2, C31.1, C32.1, IC1.4 (DGND), IC1.13 (HPGND), IC1.18 (AGND), IC1.29 (EP), IC2.4 (V-), J1.1, J2.1, J3.4, LED_DISABLE.1, LS1.2 (GND_1), LS1.3 (GND_2), LS2.2 (GND_1), LS2.3 (GND_2), R3.1, R12.1, R17.1, R22.1, U1.10 (VSS)
LRCLK: J2.6, R10.1
MCLK: J2.9, R6.1
unnamed: IC1.26 (CE), R12.2
unnamed: C8.2, C22.2, IC2.1 (OUT1), R8.2
unnamed: C22.1, IC1.23 (RIN1)
unnamed: C21.1, IC1.24 (LIN1)
unnamed: C31.2, IC1.27 (CDATA), R18.2
unnamed: C32.2, IC1.28 (CCLK), R19.2
unnamed: C11.1, C19.1, IC1.20 (VMID)
unnamed: C30.1, U1.6 (VO-)
unnamed: C5.2, C21.2, IC2.7 (OUT2), R4.2
unnamed: C30.2, U1.4 (VO+)
unnamed: C1.1, LS1.1 (DATA)
unnamed: C9.1, C17.1, IC1.17 (AVDD), R21.1
unnamed: C1.2, R1.1
unnamed: C5.1, IC2.6 (IN2-), R1.2, R4.1
unnamed: C4.1, IC2.3 (IN1+), IC2.5 (IN2+), R2.1, R3.2
unnamed: C12.1, IC1.2 (DVDD), IC1.3 (PVDD), R20.2, R22.2
unnamed: C6.1, LS2.1 (DATA)
unnamed: C6.2, R5.1
unnamed: C8.1, IC2.2 (IN1-), R5.2, R8.1
unnamed: IC1.8 (ASDOUT), R11.2
unnamed: IC1.7 (LRCK), R10.2
unnamed: C13.1, C20.1, IC1.10 (VREF)
unnamed: IC1.6 (DSDIN), R9.2
unnamed: IC1.5 (SCLK), R7.2
unnamed: D1.A, R16.1
unnamed: IC1.1 (MCLK), R6.2
unnamed: D1.C, LED_DISABLE.2
unnamed: C23.2, IC1.11 (ROUT1)
unnamed: C24.1, J1.2
unnamed: C7.1, C18.1, IC1.19 (DACVREF)
unnamed: C24.2, IC1.12 (LOUT1)
unnamed: C25.2, J3.2
unnamed: C23.1, J1.3
unnamed: C26.2, J3.3
unnamed: C27.2, J3.1
unnamed: C27.1, IC1.21 (RIN2), IC1.22 (LIN2)
unnamed: C26.1, IC1.14 (ROUT2)
unnamed: C25.1, IC1.15 (LOUT2)
RST: J4.2, R15.2, U1.9 (RES)
SCL: J2.4, R14.1, R19.1, U1.3 (SCLK/SCL)
SCLK: J2.8, R7.1
SDA: J2.3, R13.1, R18.1, U1.2 (MOSI/SDA)

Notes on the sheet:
MEMS Microphones
Dual OPA
47 microF for Headphones 1 Mic, 4 GND, 2 L, 3 R
1 microF for Line Out and Mic In
Urs Utzinger
ES8388 Codec
LP 19.4kHz Gain -1.7

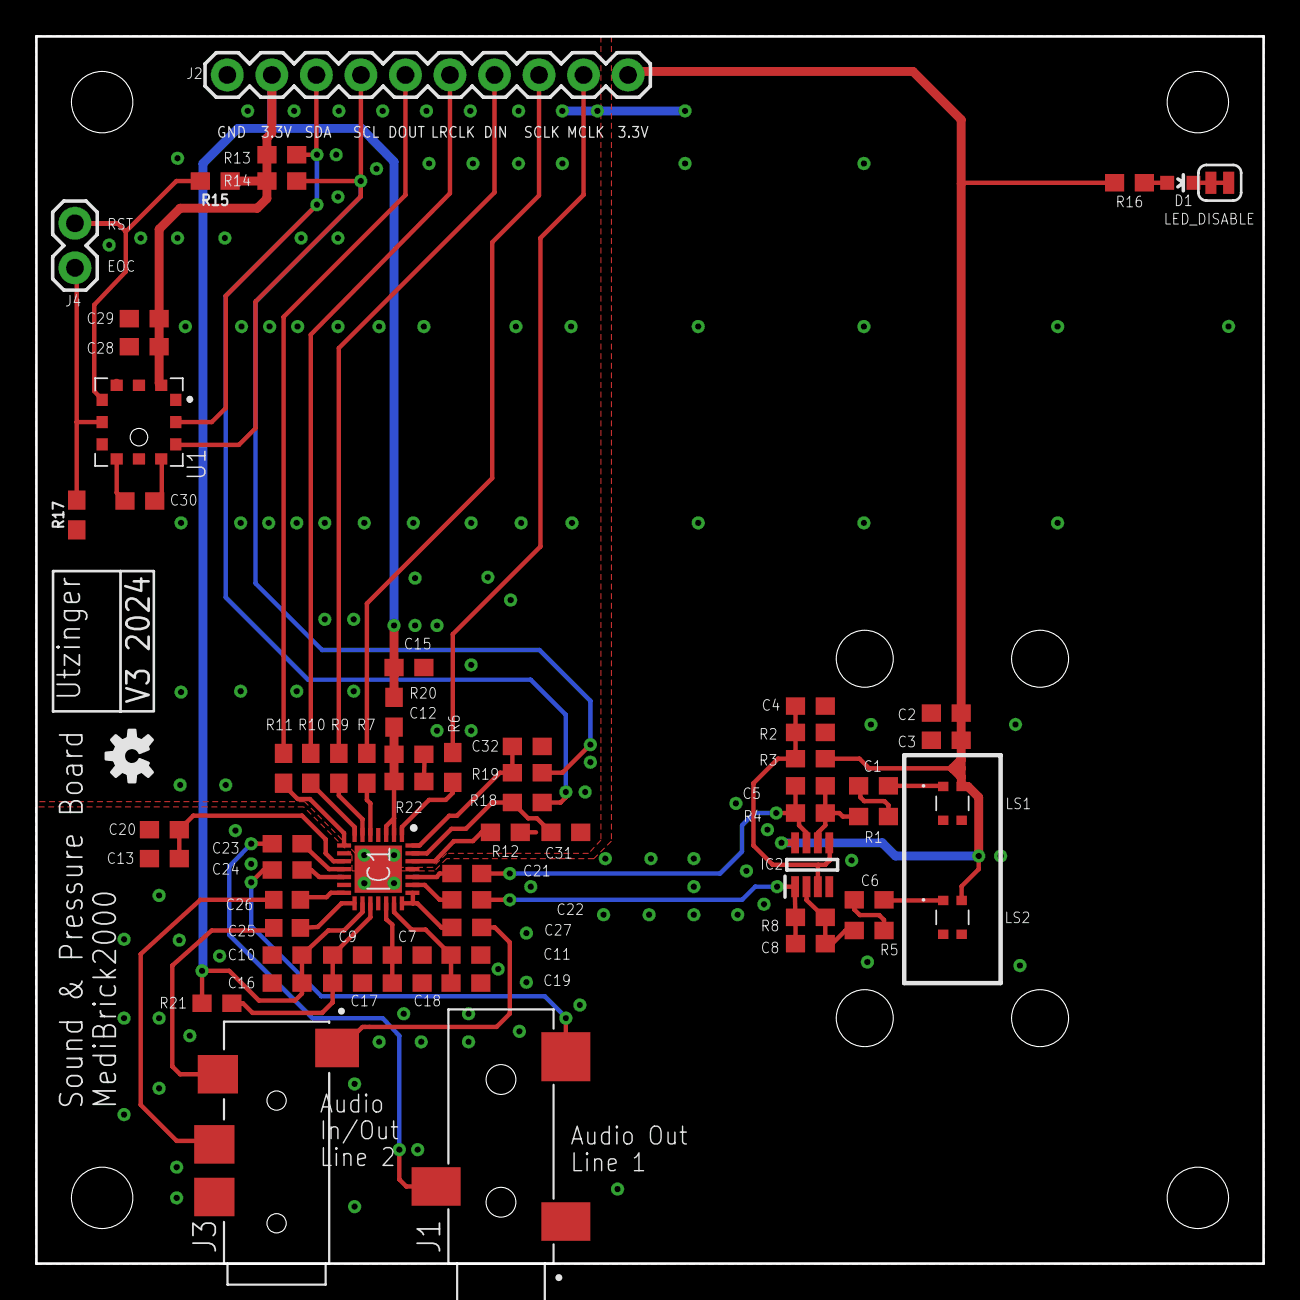
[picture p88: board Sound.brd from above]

Board: 2 copper layers, 70.0 x 70.0 mm, 66 parts (0 on the bottom side), 50 nets.

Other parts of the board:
U$3: OSHW-LOGO-S

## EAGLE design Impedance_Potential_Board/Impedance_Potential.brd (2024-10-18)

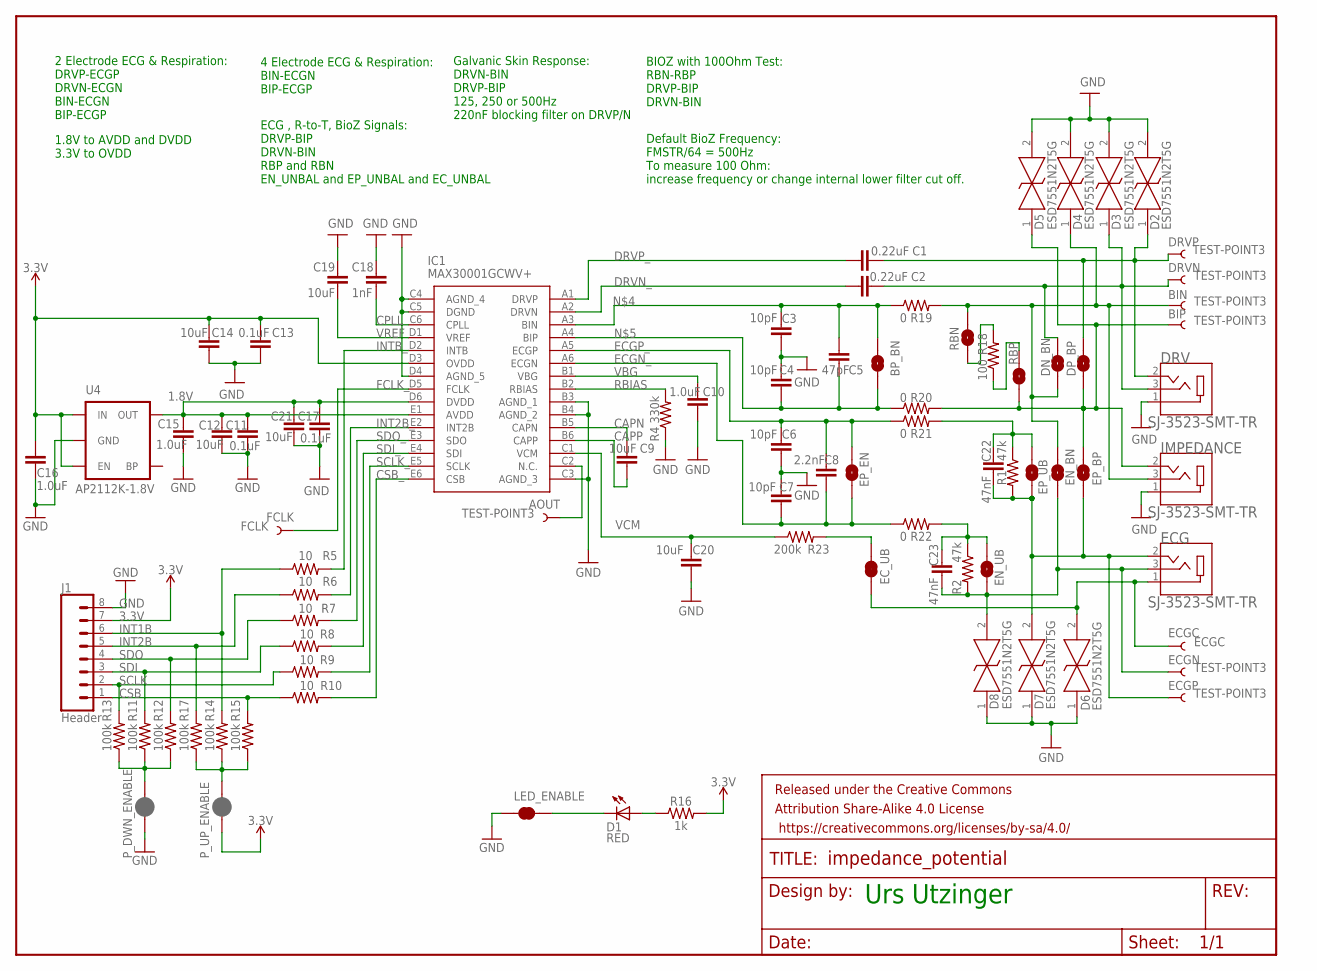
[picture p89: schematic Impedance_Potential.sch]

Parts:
AOUT: TEST-POINT3; PAD.03X.03
BIN: TEST-POINT3; PAD.03X.03
BIP: TEST-POINT3; PAD.03X.03
BP_BN: JUMPER-SMT_2_NO_SILK; SMT-JUMPER_2_NO_SILK
C1, C2: 0.22uF; 0603
C3, C4, C6, C7: 10pF; 0603
C5: 47pF; 0603
C8: 2.2nF; 0603
C9, C12, C14, C19, C20, C21: 10uF; 0603
C10, C15, C16: 1.0uF; 0603
C11, C13, C17: 0.1uF; 0603
C18: 1nF; 0603
C22, C23: 47nF; 0603
D1: RED; LED-0603
D2, D3, D4, D5, D6, D7, D8: ESD7551N2T5G
DN_BN: JUMPER-SMT_2_NO_SILK; SMT-JUMPER_2_NO_SILK
DP_BP: JUMPER-SMT_2_NO_SILK; SMT-JUMPER_2_NO_SILK
DRV: SJ-3523-SMT-TR; CUI_SJ-3523-SMT-TR
DRVN: TEST-POINT3; PAD.03X.03
DRVP: TEST-POINT3; PAD.03X.03
ECG: SJ-3523-SMT-TR; CUI_SJ-3523-SMT-TR
ECGC: ECGC; PAD.03X.03
ECGN: TEST-POINT3; PAD.03X.03
ECGP: TEST-POINT3; PAD.03X.03
EC_UB: JUMPER-SMT_2_NC_TRACE_SILK; SMT-JUMPER_2_NC_TRACE_SILK
EN_BN: JUMPER-SMT_2_NO_SILK; SMT-JUMPER_2_NO_SILK
EN_UB: JUMPER-SMT_2_NO_SILK; SMT-JUMPER_2_NO_SILK
EP_BP: JUMPER-SMT_2_NO_SILK; SMT-JUMPER_2_NO_SILK
EP_EN: JUMPER-SMT_2_NO_SILK; SMT-JUMPER_2_NO_SILK
EP_UB: JUMPER-SMT_2_NO_SILK; SMT-JUMPER_2_NO_SILK
FCLK: FCLK; PAD.03X.03
FRAME1: FRAME-LETTERNO_PACKAGE; DUMMY
IC1: MAX30001GCWV+; BGA30C50P6X5_293X274X69
IMPEDANCE: SJ-3523-SMT-TR; CUI_SJ-3523-SMT-TR
J1: Header; 1X08
LED_ENABLE: LED ENABLE; SMT-JUMPER_2_NC_TRACE_SILK
P_DWN_ENABLE: JUMPER-SMT_2_NC_PASTE_SILK; SMT-JUMPER_2_NC_PASTE_SILK
P_UP_ENABLE: JUMPER-SMT_2_NC_PASTE_SILK; SMT-JUMPER_2_NC_PASTE_SILK
R1, R2: 47k; 0603
R4: 330k; 0603
R5, R6, R7, R8, R9, R10: 10; 0603
R11, R12, R13, R14, R15, R17: 100k; 0603
R16: 1k; 0603
R18: 100; 0603
R19, R20, R21, R22: 0; 0603
R23: 200k; 0603
RBN: JUMPER-SMT_2_NO_SILK; SMT-JUMPER_2_NO_SILK
RBP: JUMPER-SMT_2_NO_SILK; SMT-JUMPER_2_NO_SILK
U4: AP2112K-1.8V; SPARKFUN-POWERIC_SOT23-5

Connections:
1.8V: C11.1, C12.1, C15.2, C17.1, C21.1, IC1.D6 (DVDD), IC1.E1 (AVDD), U4.5 (OUT)
3.3V: C13.1, C14.1, C16.2, IC1.D3 (OVDD), J1.7, P_UP_ENABLE.1, R16.2, U4.1 (IN), U4.3 (EN)
AOUT: AOUT.P$1, IC1.C2 (N.C.)
BIN: BIN.P$1, D4.1, DN_BN.1, EN_BN.2, IMPEDANCE.3, R19.2, RBN.2
BIP: BIP.P$1, D5.1, DP_BP.1, EP_BP.2, IMPEDANCE.2, R20.2, RBP.1
CAPN: C9.1, IC1.B5 (CAPN)
CAPP: C9.2, IC1.B6 (CAPP)
CPLL: C18.2, IC1.C6 (CPLL)
CSB: J1.1, R10.1, R15.2
CSB_: IC1.E6 (CSB), R10.2
DRVN: C2.2, D3.1, DN_BN.2, DRV.3, DRVN.P$1
DRVN_: C2.1, IC1.A2 (DRVN)
DRVP: C1.2, D2.1, DP_BP.2, DRV.2, DRVP.P$1
DRVP_: C1.1, IC1.A1 (DRVP)
ECGC: D6.2, ECG.1, ECGC.P$1, EC_UB.1
ECGN: C23.2, D8.2, ECG.3, ECGN.P$1, EN_BN.1, EN_UB.1, R2.2
ECGN_: C7.2, C8.2, EP_EN.1, IC1.A6 (ECGN), R22.1
ECGP: C22.2, D7.2, ECG.2, ECGP.P$1, EP_BP.1, EP_UB.1, R1.2
ECGP_: C6.1, C8.1, EP_EN.2, IC1.A5 (ECGP), R21.1
FCLK_: FCLK.P$1, IC1.D5 (FCLK)
GND: C3.2, C4.1, C6.2, C7.1, C10.2, C11.2, C12.2, C13.2, C14.2, C15.1, C16.1, C17.2, C18.1, C19.1, C20.2, C21.2, D2.2, D3.2, D4.2, D5.2, D6.1, D7.1, D8.1, DRV.1, IC1.B3 (AGND_1), IC1.B4 (AGND_2), IC1.C3 (AGND_3), IC1.C4 (AGND_4), IC1.C5 (DGND), IC1.D4 (AGND_5), IMPEDANCE.1, J1.8, LED_ENABLE.1, P_DWN_ENABLE.1, R4.1, U4.2 (GND)
INT1B: J1.6, R5.1, R14.2
INT2B: J1.5, R6.1, R17.2
INT2B_: IC1.E2 (INT2B), R6.2
INTB_: IC1.D2 (INTB), R5.2
unnamed: C23.1, EN_UB.2, R2.1, R22.2
unnamed: EC_UB.2, R23.2
unnamed: C22.1, EP_UB.2, R1.1, R21.2
unnamed: BP_BN.2, C3.1, C5.1, IC1.A3 (BIN), R19.1
unnamed: BP_BN.1, C4.2, C5.2, IC1.A4 (BIP), R20.1
unnamed: D1.A, R16.1
unnamed: D1.C, LED_ENABLE.2
unnamed: P_DWN_ENABLE.2, R11.1, R12.1, R13.1
unnamed: P_UP_ENABLE.2, R14.1, R15.1, R17.1
unnamed: R18.2, RBN.1
unnamed: R18.1, RBP.2
RBIAS: IC1.B2 (RBIAS), R4.2
SCLK: J1.2, R9.1, R13.2
SCLK_: IC1.E5 (SCLK), R9.2
SDI: J1.3, R8.1, R11.2
SDI_: IC1.E4 (SDI), R8.2
SDO: J1.4, R7.1, R12.2
SDO_: IC1.E3 (SDO), R7.2
VBG: C10.1, IC1.B1 (VBG)
VCM: C20.1, IC1.C1 (VCM), R23.1
VREF: C19.2, IC1.D1 (VREF)

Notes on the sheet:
2 Electrode ECG & Respiration: DRVP-ECGP DRVN-ECGN BIN-ECGN BIP-ECGP
4 Electrode ECG & Respiration: BIN-ECGN BIP-ECGP
Galvanic Skin Response: DRVN-BIN DRVP-BIP 125, 250 or 500Hz 220nF blocking filter on DRVP/N
BIOZ with 100Ohm Test: RBN-RBP DRVP-BIP DRVN-BIN
1.8V to AVDD and DVDD 3.3V to OVDD
ECG , R-to-T, BioZ Signals: DRVP-BIP DRVN-BIN RBP and RBN EN_UNBAL and EP_UNBAL and EC_UNBAL
Default BioZ Frequency: FMSTR/64 = 500Hz To measure 100 Ohm: increase frequency or change internal lower filter cut off.
Urs Utzinger

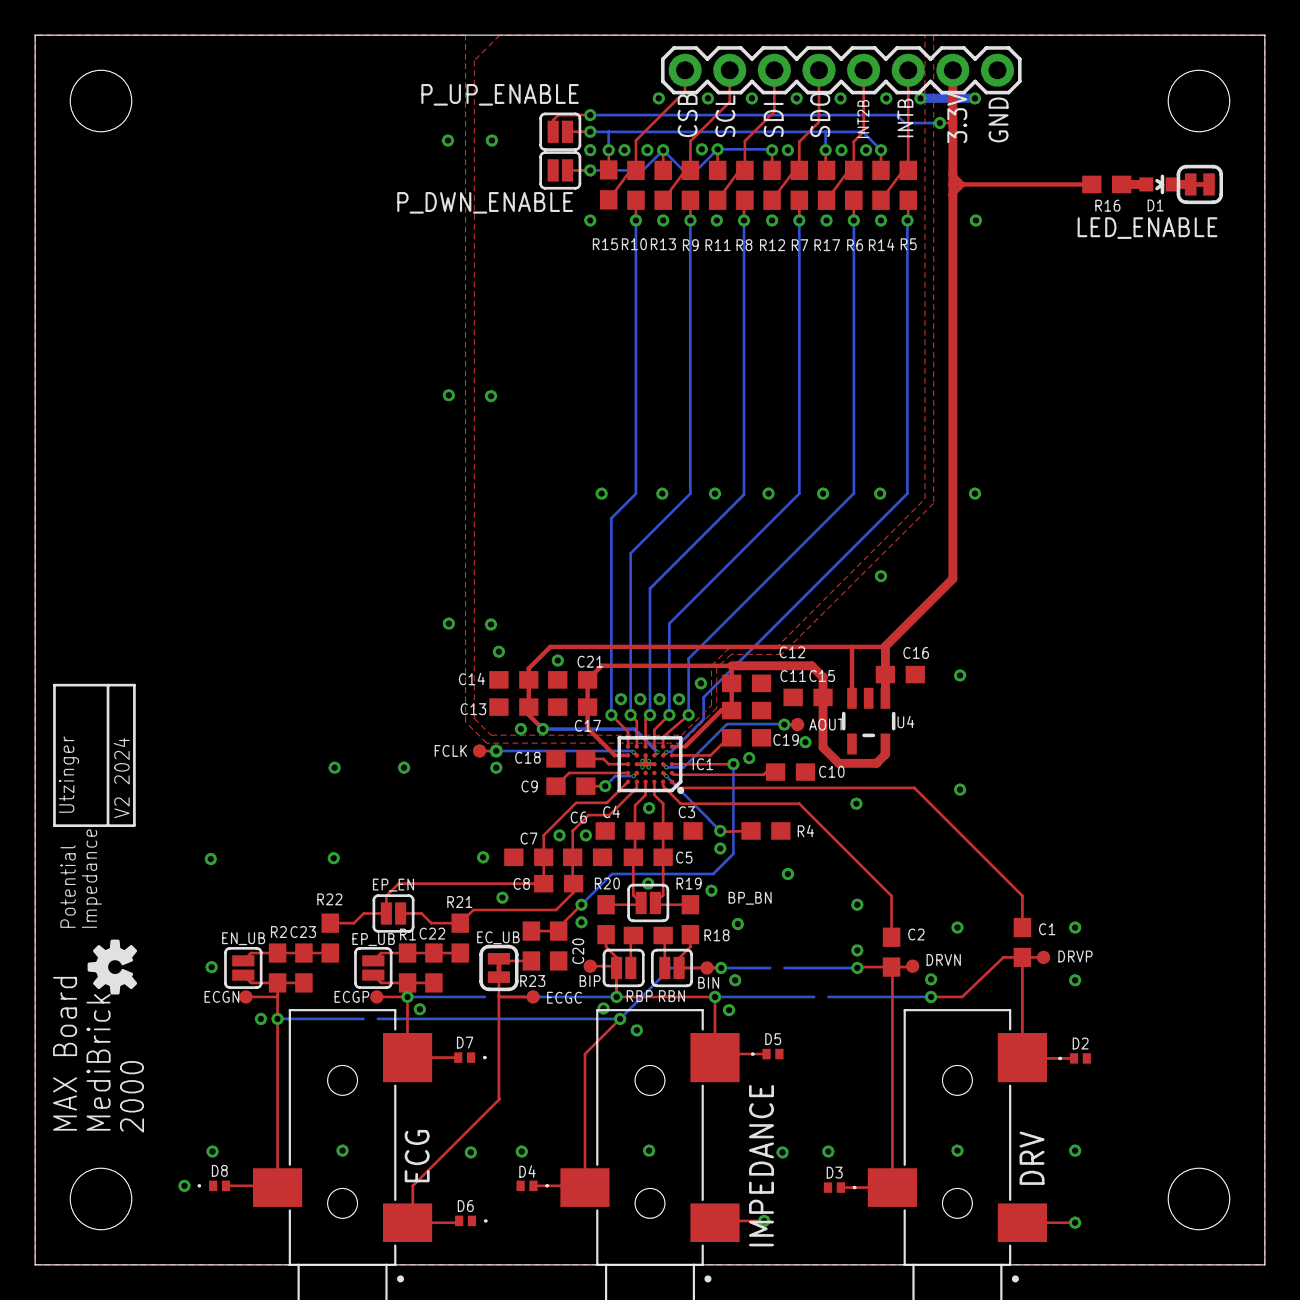
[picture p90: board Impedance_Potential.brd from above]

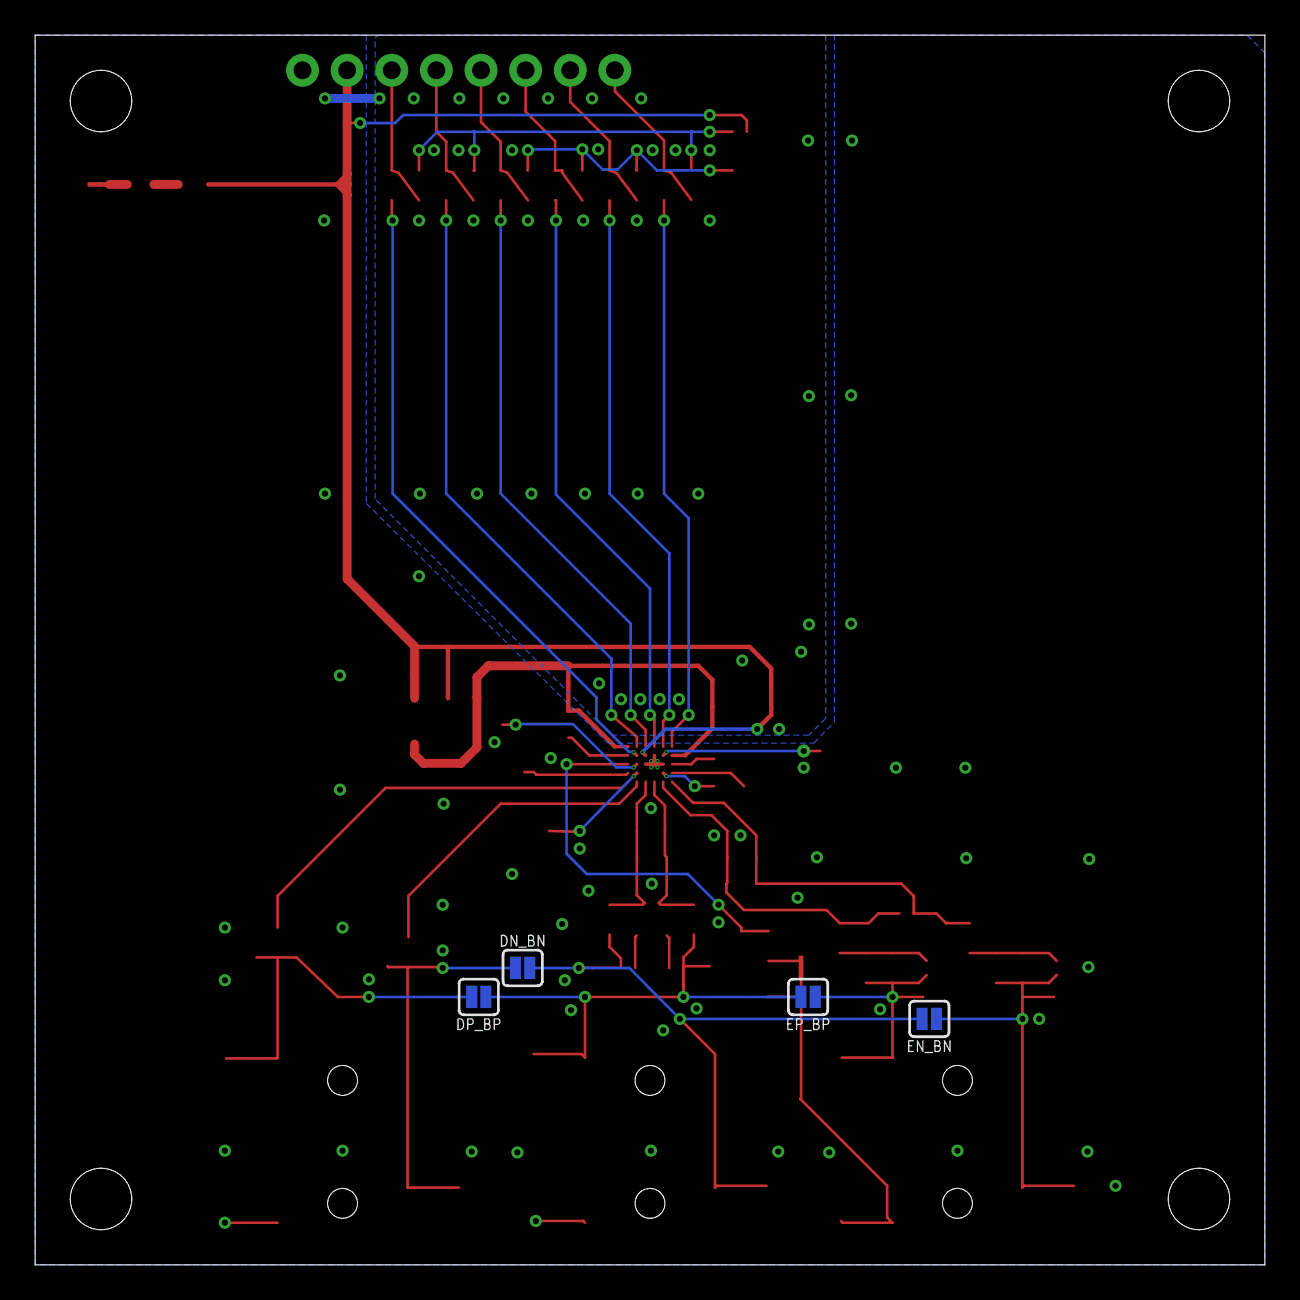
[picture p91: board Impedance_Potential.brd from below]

Board: 2 copper layers, 70.0 x 70.0 mm, 84 parts (4 on the bottom side), 46 nets.

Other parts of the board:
U$1: OSHW-LOGO-S

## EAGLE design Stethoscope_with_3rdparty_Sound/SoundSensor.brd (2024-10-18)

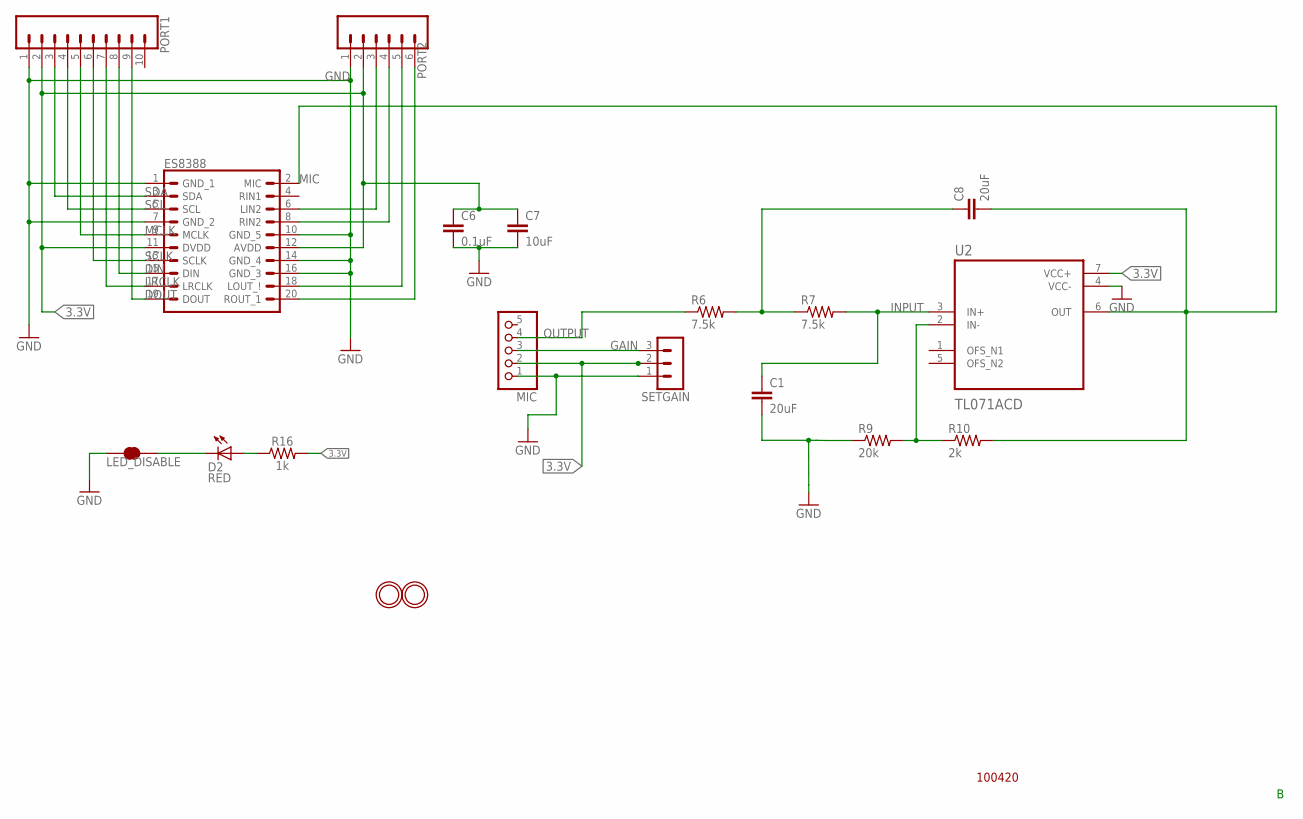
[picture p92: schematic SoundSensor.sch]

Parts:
C1, C8: 20uF; C0603
C6: 0.1uF; C0603
C7: 10uF; C0603
D2: RED; LED-0603
ES8388: ES8388ES8388; ES8388
LED_DISABLE: JUMPER-SMT_2_NC_TRACE_SILK; SMT-JUMPER_2_NC_TRACE_SILK
MIC: HEADER-1X576MIL; 1X05_ROUND_76
PORT1: CONN_10"; 1X10
PORT2: CONN_06SILK_FEMALE_PTH; 1X06
R6, R7: 7.5k; R0603
R9: 20k; R0603
R10: 2k; R0603
R16: 1k; 0603
SETGAIN: MA03-1
U2: TL071ACD; SOIC127P599X175-8N
U$1, U$5: MOUNTINGHOLE2.0; MOUNTINGHOLE_2.0_PLATED

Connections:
3.3V: C6.1, C7.1, ES8388.11 (DVDD), ES8388.12 (AVDD), MIC.2, PORT1.2, PORT2.2, R16.2, SETGAIN.2, U2.7 (VCC+)
DIN: ES8388.15 (DIN), PORT1.8
DOUT: ES8388.19 (DOUT), PORT1.9
GAIN: MIC.3, SETGAIN.3
GND: C1.2, C6.2, C7.2, ES8388.1 (GND_1), ES8388.7 (GND_2), ES8388.10 (GND_5), ES8388.14 (GND_4), ES8388.16 (GND_3), LED_DISABLE.1, MIC.1, PORT1.1, PORT2.1, R9.1, SETGAIN.1, U2.4 (VCC-)
INPUT: C1.1, R7.2, U2.3 (IN+)
LRCLK: ES8388.17 (LRCLK), PORT1.7
MCLK: ES8388.9 (MCLK), PORT1.5
MIC: C8.2, ES8388.2 (MIC), R10.2, U2.6 (OUT)
unnamed: ES8388.6 (LIN2), PORT2.3
unnamed: ES8388.8 (RIN2), PORT2.4
unnamed: ES8388.18 (LOUT_!), PORT2.5
unnamed: ES8388.20 (ROUT_1), PORT2.6
unnamed: C8.1, R6.2, R7.1
unnamed: R9.2, R10.1, U2.2 (IN-)
unnamed: D2.A, R16.1
unnamed: D2.C, LED_DISABLE.2
OUTPUT: MIC.4, R6.1
SCL: ES8388.5 (SCL), PORT1.4
SCLK: ES8388.13 (SCLK), PORT1.6
SDA: ES8388.3 (SDA), PORT1.3

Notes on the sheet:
100420

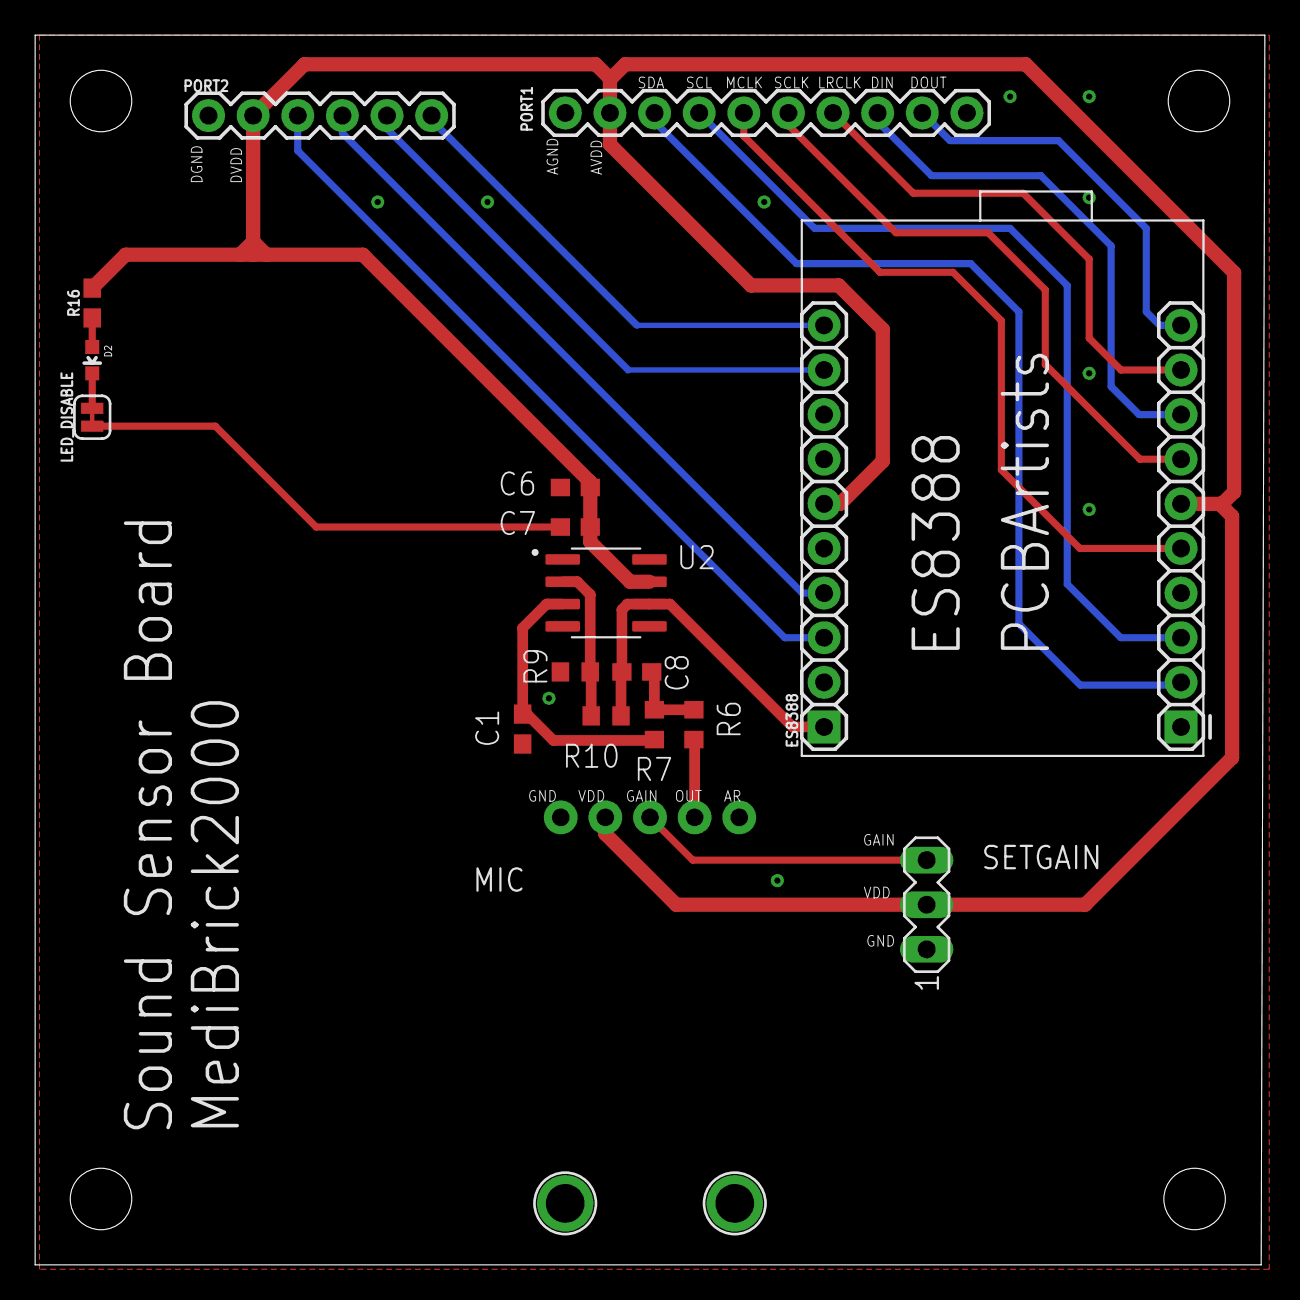
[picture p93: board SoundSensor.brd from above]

Board: 2 copper layers, 70.0 x 70.0 mm, 19 parts (0 on the bottom side), 21 nets.

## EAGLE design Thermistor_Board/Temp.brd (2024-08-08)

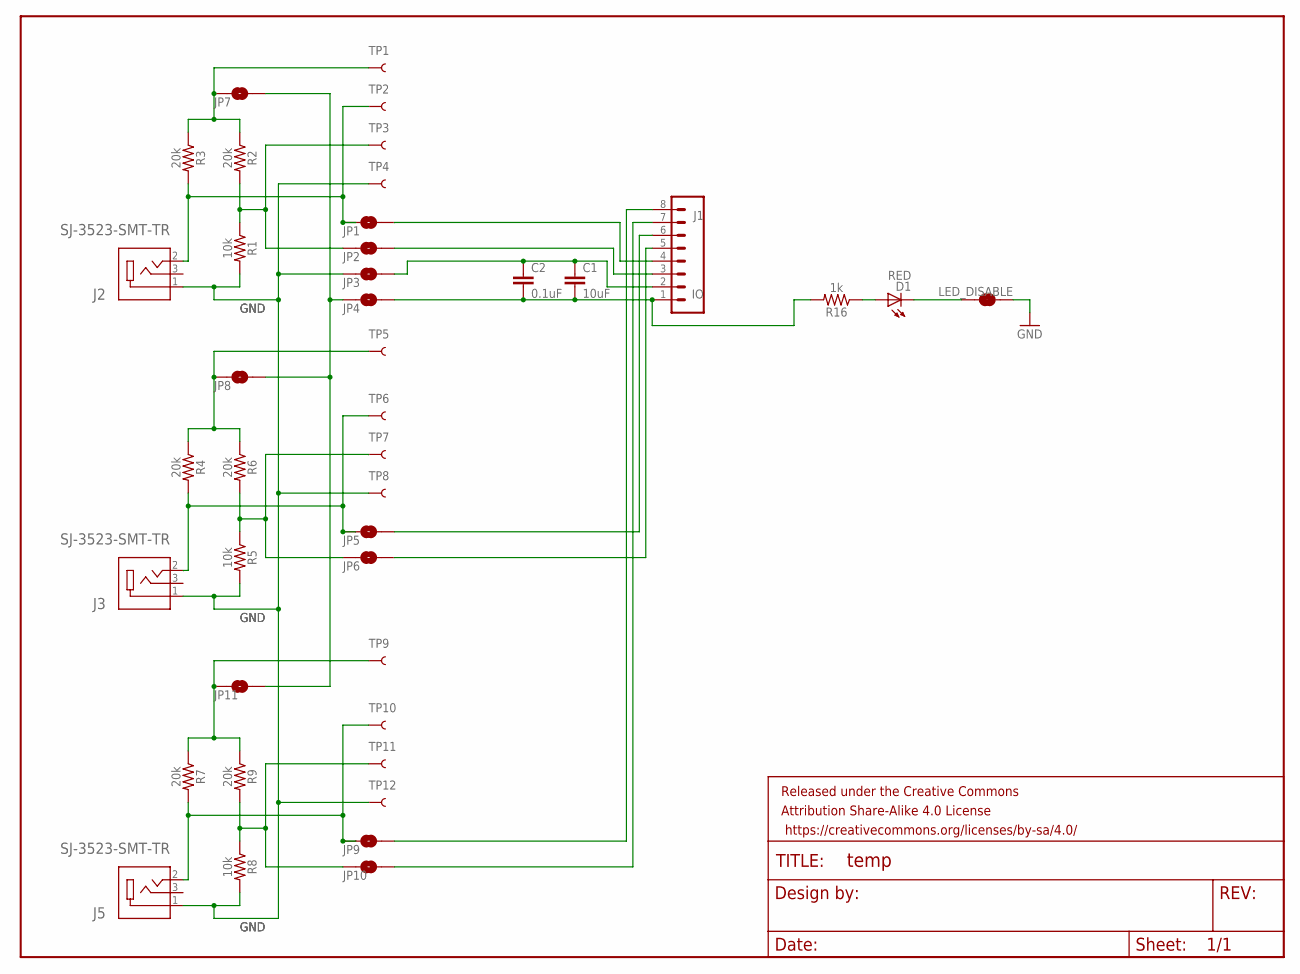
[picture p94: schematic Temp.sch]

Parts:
C1: 10uF; 0603
C2: 0.1uF; 0603
D1: RED; LED-0603
FRAME1: FRAME-LETTERNO_PACKAGE; DUMMY
J1: IO; 1X08
J2, J3, J5: SJ-3523-SMT-TR; CUI_SJ-3523-SMT-TR
JP1, JP2, JP3, JP4, JP5, JP6, JP7, JP8, JP9, JP10, JP11: JUMPER-SMT_2_NO_NO-SILK; SMT-JUMPER_2_NO_NO-SILK
LED_DISABLE: JUMPER-SMT_2_NC_TRACE_SILK; SMT-JUMPER_2_NC_TRACE_SILK
R1, R5, R8: 10k; 0603
R2, R3, R4, R6, R7, R9: 20k; 0603
R16: 1k; 0603
TP1, TP2, TP3, TP4, TP5, TP6, TP7, TP8, TP9, TP10, TP11, TP12: TEST-POINT3X5; PAD.03X.05

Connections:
3.3V: JP4.1, JP7.2, JP8.2, JP11.2
GND: J2.1, J3.1, J5.1, JP3.1, LED_DISABLE.1, R1.2, R5.2, R8.2, TP4.P$1, TP8.P$1, TP12.P$1
unnamed: JP6.1, R5.1, R6.2, TP7.P$1
unnamed: J1.5, JP6.2
unnamed: JP2.1, R1.1, R2.2, TP3.P$1
unnamed: JP7.1, R2.1, R3.1, TP1.P$1
unnamed: J1.3, JP2.2
unnamed: J2.2, JP1.1, R3.2, TP2.P$1
unnamed: J1.4, JP1.2
unnamed: J3.2, JP5.1, R4.2, TP6.P$1
unnamed: J1.7, JP10.2
unnamed: J1.8, JP9.2
unnamed: J1.6, JP5.2
unnamed: JP8.1, R4.1, R6.1, TP5.P$1
unnamed: JP10.1, R8.1, R9.2, TP11.P$1
unnamed: J5.2, JP9.1, R7.2, TP10.P$1
unnamed: C1.1, C2.1, J1.2, JP3.2
unnamed: JP11.1, R7.1, R9.1, TP9.P$1
unnamed: C1.2, C2.2, J1.1, JP4.2, R16.2
unnamed: D1.A, R16.1
unnamed: D1.C, LED_DISABLE.2

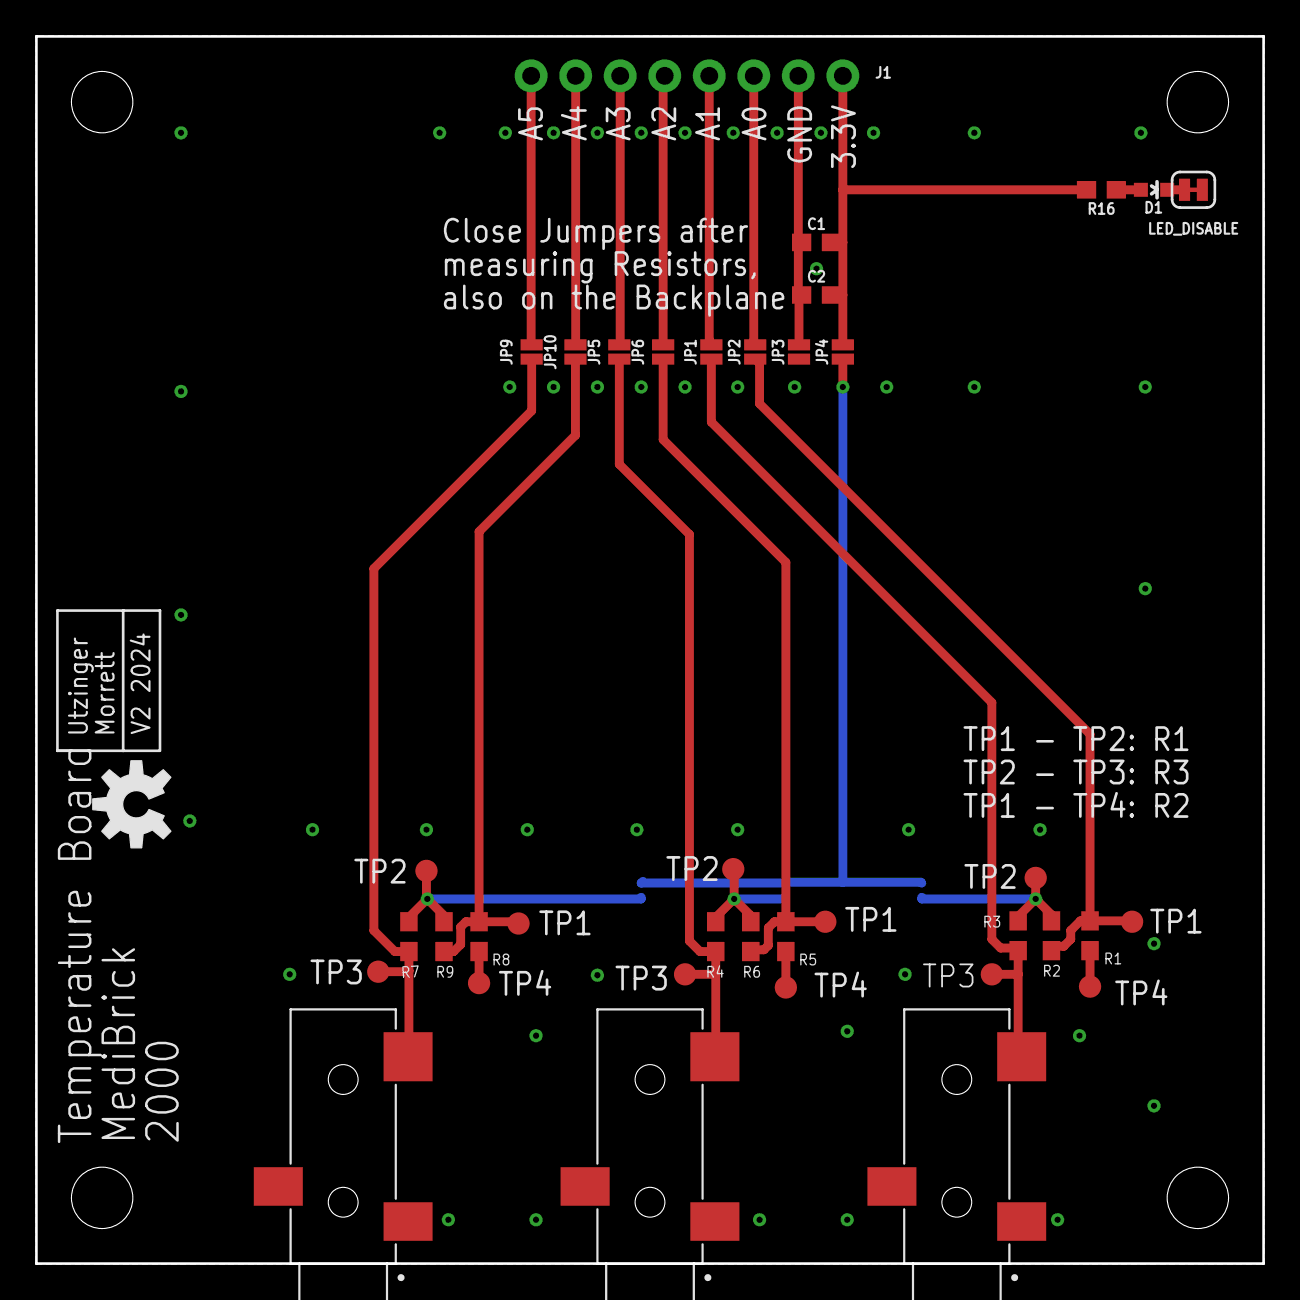
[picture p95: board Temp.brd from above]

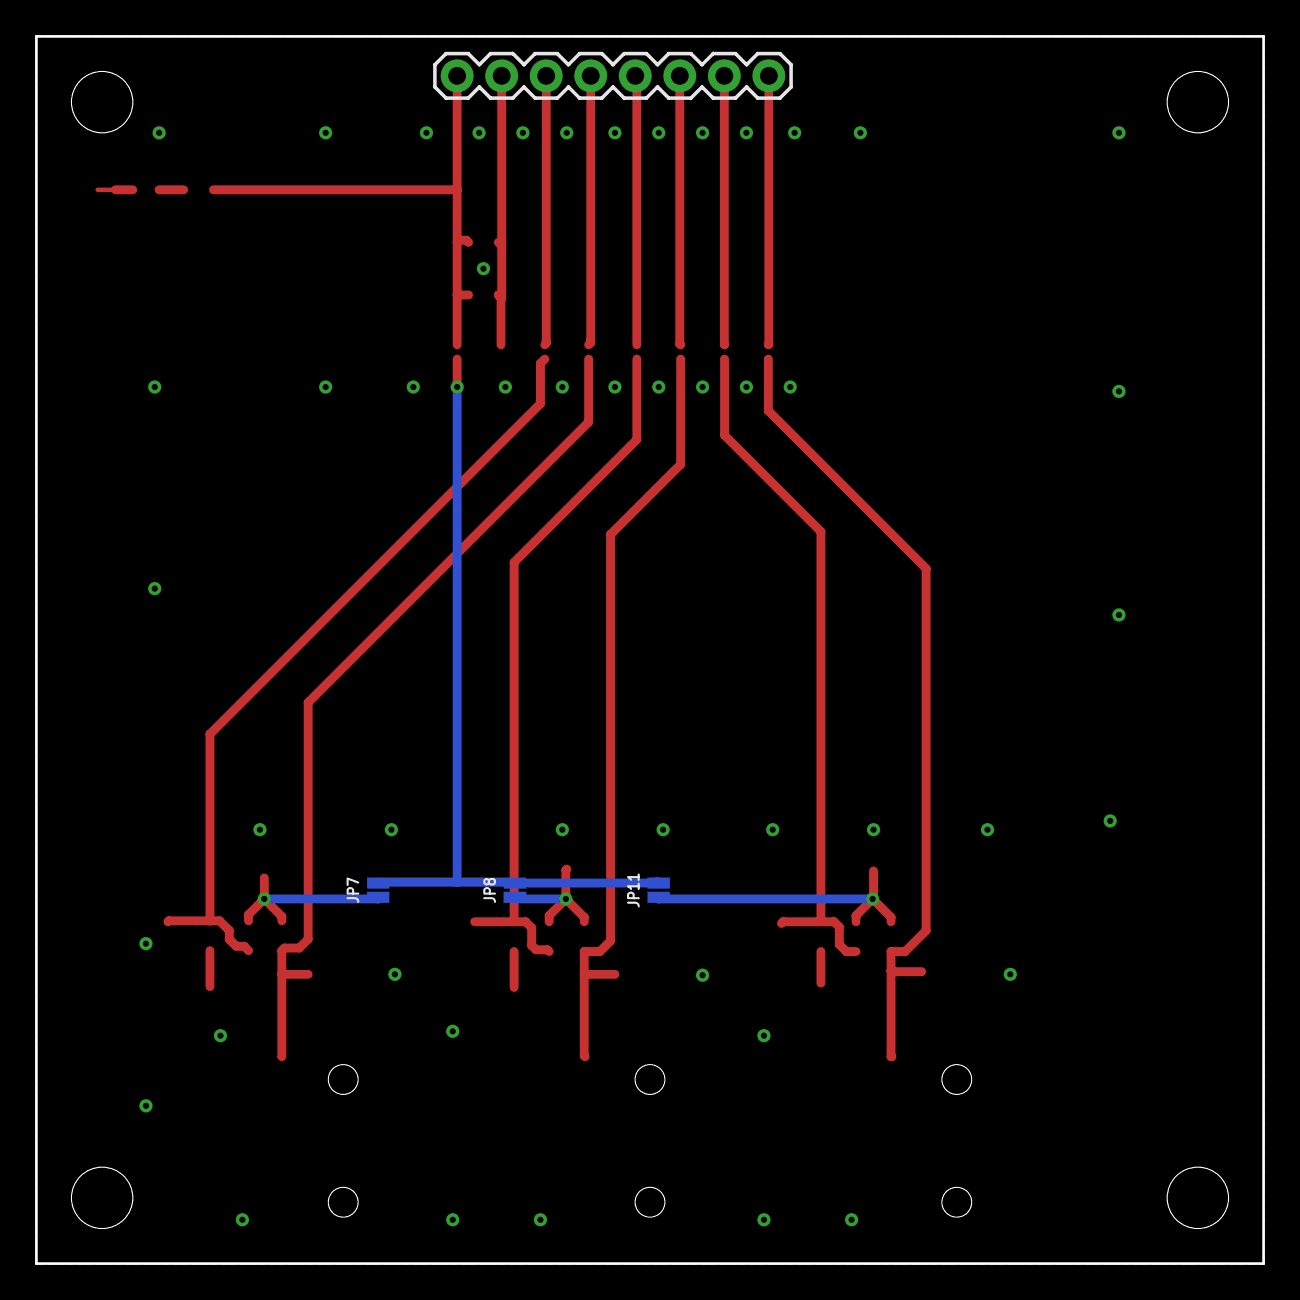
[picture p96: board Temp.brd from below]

Board: 2 copper layers, 70.0 x 70.0 mm, 43 parts (4 on the bottom side), 21 nets.

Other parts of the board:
U$1: OSHW-LOGO-M

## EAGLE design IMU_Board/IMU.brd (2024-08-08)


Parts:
C1, C2, C3, C4, C5, C13, C17: 0.1uF; 0603
C14, C21: 10uF; 0603@1
C15, C16: 1.0uF; 0603
D1: RED; LED-0603
FRAME1: FRAME-LETTERNO_PACKAGE; DUMMY
J1: Header; 1X09
LED: LED ENABLE; SMT-JUMPER_2_NC_TRACE_SILK
PDWN: JUMPER-SMT_2_NC_PASTE_SILK; SMT-JUMPER_2_NC_PASTE_SILK
PUP: JUMPER-SMT_2_NC_TRACE_SILK; SMT-JUMPER_2_NC_TRACE_SILK
Q1, Q2, Q3, Q4, Q5: BSS138; SPARKFUN_SOT23-3
R1, R2, R3, R4, R11, R12, R13, R15, R17, R18, R19, R20, R21, R22, R23, R24, R25: 10k; 0603
R5, R6, R7, R8, R9, R10, R14, R27, R28: 10; 0603
R16: 1k; 0603
U1: ICM-20948; QFN40P300X300X105-24N
U3: BMP581
U4: AP2112K-1.8V; SPARKFUN-POWERIC_SOT23-5

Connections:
1.8V: C2.1, C15.2, C17.1, C21.1, Q1.1 (G), Q2.1 (G), Q3.1 (G), Q4.1 (G), Q5.1 (G), R1.1, R3.1, R18.1, R20.1, R22.1, U1.8 (VDDIO), U4.5 (OUT)
3.3V: C3.1, C13.1, C14.1, C16.2, J1.8, PUP.1, R2.1, R4.1, R5.2, R14.1, R16.2, R19.1, R21.1, R23.1, U1.13 (VDD), U4.1 (IN), U4.3 (EN)
CS_581: J1.2, R9.1, R24.2
CS_581_HV: R9.2, U3.6 (CSB)
CS_20948: J1.6, R15.2, R27.1
CS_20948_HV: Q1.3 (D), R4.2, R27.2
CS_20948_LV: Q1.2 (S), R3.2, U1.22 (!CS)
GND: C1.2, C2.2, C3.2, C4.2, C5.2, C13.2, C14.2, C15.1, C16.1, C17.2, C21.2, J1.9, LED.1, PDWN.1, U1.11 (FSYNC), U1.18 (GND), U1.20 (RESV_20), U3.3 (VSS_1), U3.8 (VSS_2), U3.9 (VSS_3), U4.2 (GND)
INT_581: J1.1, R10.1, R17.2
INT_581_HV: R10.2, U3.7 (INT)
INT_20948: J1.7, R25.2, R28.1
INT_20948_HV: Q5.3 (D), R23.2, R28.2
INT_20948_LV: Q5.2 (S), R22.2, U1.12 (INT1)
unnamed: C1.1, U1.10 (REGOUT)
unnamed: D1.A, R16.1
unnamed: D1.C, LED.2
unnamed: PDWN.2, R11.1, R12.1, R13.1
unnamed: PUP.2, R15.1, R17.1, R24.1, R25.1
SCL: J1.5, R6.1, R12.2
SCL_HV: Q2.3 (D), R2.2, R6.2, U3.2 (SCK)
SDI: J1.4, R7.1, R11.2
SDI_HV: Q3.3 (D), R7.2, R19.2, U3.4 (SDI)
SDI_LV: Q3.2 (S), R18.2, U1.24 (SDA/SDI)
SDO: J1.3, R8.1, R13.2
SDO_HV: Q4.3 (D), R8.2, R21.2, U3.5 (SDO)
SDO_LV: Q4.2 (S), R20.2, U1.9 (AD0/SDO)
SLCK_LV: Q2.2 (S), R1.2, U1.23 (SCL/SCLK)
VDD: C4.1, R5.1, U3.10 (VDD)
VDDIO: C5.1, R14.2, U3.1 (VDDIO)

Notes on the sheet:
Urs Utzinger
Possible Improvements: - VDD in ICM can also go to 1.8V - FSYNC should be provided as input and pulled low - 10K resistors could be combined into chip with multiple resistor - level shifter should be combined into chip with 2 or more shifters (BSS138) - pull down at connector might not be needed. -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


Board: 2 copper layers, 70.0 x 70.0 mm, 53 parts (0 on the bottom side), 29 nets.

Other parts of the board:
U$1: OSHW-LOGO-S

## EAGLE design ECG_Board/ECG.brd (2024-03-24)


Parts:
D1: RED; LED-0603
FRAME1: FRAME-LETTERNO_PACKAGE; DUMMY
JP2: M06SIP; 1X06
JP4: M03PTH; 1X03
LED_DISABLE: JUMPER-SMT_2_NC_TRACE_SILK; SMT-JUMPER_2_NC_TRACE_SILK
R16: 1k; 0603
U$1: SPARK_ECG

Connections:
3.3V: JP2.2, R16.2, U$1.2 (3.3V)
GND: JP2.1, LED_DISABLE.1, U$1.1 (GND)
unnamed: JP4.1, U$1.7 (RA)
unnamed: JP4.2, U$1.8 (LA)
unnamed: JP4.3, U$1.9 (RL)
unnamed: JP2.6, U$1.6 (!SDN)
unnamed: JP2.5, U$1.5 (LO+)
unnamed: JP2.4, U$1.4 (LO-)
unnamed: JP2.3, U$1.3 (OUT)
unnamed: D1.A, R16.1
unnamed: D1.C, LED_DISABLE.2


Board: 2 copper layers, 70.0 x 70.0 mm, 8 parts (0 on the bottom side), 11 nets.

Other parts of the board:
U$2: OSHW-LOGO-M

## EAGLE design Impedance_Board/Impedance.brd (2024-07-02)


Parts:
AD5933: ANALOG_DEVICES_AD5933YRSZANALOG_DEVICES_AD5933YRS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; ANALOG_DEVICES_AD5933YRSZ_0
C1, C4, C6, C8, C12: 0.1uF; 0603
C2, C5, C9, C13: 10uF; 0603
C3: 10nF; 0603
CAL_INT: PINHD-1X1; 1X01
CAL_RES1: 2K; R0603
D1: RED; LED-0603
EXCITE: SJ-3523-SMT-TR; CUI_SJ-3523-SMT-TR
FRAME1: FRAME-LETTERNO_PACKAGE; DUMMY
I2C_IN, I2C_OUT: STEMMA_I2C_QTRA; JST_SH4_RA
IC1: AD8608ARZ; SOIC127P600X175-14N
IC2: INA826AID; SOIC127P600X175-8N
J1: CONN_04; 1X04
JP1, JP2: JUMPER-SMT_3_1-NC_TRACE_NO-SILK; SMT-JUMPER_3_1-NC_TRACE_NO-SILK
MEASURE: SJ-3523-SMT-TR; CUI_SJ-3523-SMT-TR
R1, R2: 4.7k; 0603
R3, R4: 20k; 0603
R5, R6: 100k; 0603
R7: 200k; 0603
R8, R14, R16: 1k; 0603
R9, R10: 10k; 0603
R11: 270k; 0603
SINGLE_PUG: SJ-3523-SMT-TR; CUI_SJ-3523-SMT-TR
SJ4: LED DISABLE; SMT-JUMPER_2_NC_TRACE_SILK
TP1: TEST-POINT3X5; PAD.03X.05
U4: MC74VHC1GT66DTT1; TSOP5_1P65X3P15_ONS

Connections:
3.3V: AD5933.9 (DVDD), AD5933.10 (AVDD1), AD5933.11 (AVDD2), C1.1, C2.1, C4.1, C5.1, C6.1, C8.1, C9.1, C12.1, C13.1, I2C_IN.2 (V+), I2C_OUT.2 (V+), IC1.4 (V+), IC2.8 (+VS), J1.2, R1.2, R2.2, R5.1, R9.2, R16.2, U4.5
GND: AD5933.12 (DGND), AD5933.13 (AGND1), AD5933.14 (AGND2), C1.2, C2.2, C4.2, C5.2, C6.2, C8.2, C9.2, C12.2, C13.2, EXCITE.1, I2C_IN.1 (GND), I2C_OUT.1 (GND), IC1.11 (V-), IC2.5 (-VS), J1.1, MEASURE.1, R6.2, R10.1, SINGLE_PUG.1, SJ4.1, U4.3
MCLK: AD5933.8 (MCLK), TP1.P$1
unnamed: IC1.6 (-IN_B), R7.1, SINGLE_PUG.3
unnamed: CAL_INT.1, U4.4
unnamed: IC1.7 (OUT_B), JP2.3, R7.2
unnamed: JP2.2, R4.2
unnamed: AD5933.4 (RFB), R3.1
unnamed: C3.2, IC1.3 (+IN_A), R5.2, R6.1
unnamed: JP1.1, R11.1
unnamed: IC1.1 (OUT_A), IC1.2 (-IN_A), JP1.2
unnamed: IC2.7 (VOUT), JP2.1
unnamed: IC1.12 (+IN_D), R9.1, R10.2
unnamed: JP1.3, SINGLE_PUG.2
unnamed: IC1.5 (+IN_B), IC1.10 (+IN_C), IC1.13 (-IN_D), IC1.14 (OUT_D), IC2.6 (REF)
unnamed: EXCITE.2, IC1.9 (-IN_C), R11.2, R14.1
unnamed: IC2.4 (+IN), MEASURE.2
unnamed: IC2.1 (-IN), MEASURE.3
unnamed: IC2.2 (RG_1), R8.2
unnamed: IC2.3 (RG_2), R8.1
unnamed: CAL_RES1.2, U4.1
unnamed: EXCITE.3, IC1.8 (OUT_C), R14.2
unnamed: D1.A, R16.1
unnamed: D1.C, SJ4.2
SCL: AD5933.16 (SCL), I2C_IN.4 (SCL), I2C_OUT.4 (SCL), J1.4, R1.1
SDA: AD5933.15 (SDA), I2C_IN.3 (SDA), I2C_OUT.3 (SDA), J1.3, R2.1
VIN: AD5933.5 (VIN), CAL_RES1.1, R3.2, R4.1
VOUT: AD5933.6 (VOUT), C3.1, U4.2

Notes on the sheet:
High Pass Filter
Vref
Transimpedance Measure
Transimpedance Excite
Single Plug Impedance
STEMMA QT Connectors
I2C Through-Holes
Switch Direct vs Transimpedance
Amp_VCC
Amp_REFGEN
Amp_Buffer
AMP_FB



Board: 2 copper layers, 70.0 x 70.0 mm, 42 parts (2 on the bottom side), 28 nets.

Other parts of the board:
U$2: OSHW-LOGO-M

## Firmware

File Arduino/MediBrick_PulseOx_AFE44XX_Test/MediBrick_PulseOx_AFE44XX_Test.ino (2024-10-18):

/******************************************************************************************************/
// AFE44XX Test Program
// 
// Allows User to Experiment with Settings for Pulse Oximeter AFE during runtime through terminal.
//
// In additions this program shows how to
//   - Startup and Configure AFE
//   - Inspect Registers
//   - Run Diagnostics
//   - Read background subtracted IR and RED readings continously
//
// The AFE functions are organized into the following groups:
//   - Photodiode receiver settings
//     - Transimpedance amplifier feedback resistor and capacitor
//     - Second amplifier stage gain
//   - LED transmitter settings
//     - Infrared and red LED power settings
//   - Timing
//     - Program timing settings from the AFE4490 datasheet
//       Modify default settings by a linear factor but maintaining ADC reset pulse, sampling offset and conversion offset
//     - Averaging of readings
//   - All other hardware options
//
// Urs Utzinger 2024
/******************************************************************************************************/

// Includes
// ---------
#include <Arduino.h>
#include <stdlib.h> 
#include "afe44xx.h"
#include "logger.h"

// Select the  defaultlog level, you can change this at runtime also
// #define LOG_LEVEL LOG_LEVEL_NONE 
// #define LOG_LEVEL LOG_LEVEL_ERROR
// #define LOG_LEVEL LOG_LEVEL_WARN 
#define LOG_LEVEL LOG_LEVEL_INFO 
// #define LOG_LEVEL LOG_LEVEL_DEBUG

// Serial
#define BAUD_RATE 500000  // Up to 2,000,000 on ESP32, however more than 500 kBaud might be unreliable

// Hardware Pin Connection
// -----------------------
// Check assembly instructions for https://github.com/uutzinger/BioMedicalSensorBoard/blob/main/SPO2_Board/assembly.md
// DRDY, CS, PWDN connection are required for this software to run.
// If you do not want to use data ready interrupt, you can poll the data directly from the registers.
//

// For ESP32 Thing Plus C
// #define RESET_PIN    19  // active low, hardware reset, use if SPI not longer works with the sensor

// For feather ES32 S3
#define RESET_PIN    10  // active low, hardware reset, use if SPI not longer works with the sensor

// Same on both boards
#define DRDY_PIN     13  // data ready interrupt from AFE
#define CS_PIN        6  // chip select, active low, needed for SPI, you can hardwire this pin or activate when you have multipole SPI devices
#define PDALARM_PIN  12  // Photodiode Alarm pin, this can also be used to show activity of the AFE measurement process
#define LEDALARM_PIN  9  // LED Alarm pin, this can also be used to show activity of the AFE measurement process
#define DIAGEND_PIN  11  // This can be used to wait until diagnosis is finished, but it is usually not necessary
#define PWDN_PIN      5  // power down pin, active low, you can hardwire for always on and turn off LED, Photodiode and other hardware with software


// AFE Global Configuration Variables
// ----------------------------------
// these are needed for interactive user programming during runtime
/* Diagnostics */
uint32_t afe44xx_diag_status;         // holds results of the diagnosis function
/* Report data */
bool    afe44xx_reporting    = false; // continously report IR and red measurements on serial port
bool    afe44xx_reporting_simple = false; // continously report IR and red measurements on serial port
/* Receiver Stage  */
bool    afe44xx_sameGain     = true;  // same gain and feddback ressistor/capacitor for LED1 and LED2
int8_t  afe44xx_stage2Gain1  = 0;     // stage 2 gain for LED1: -1 disable, 0=1, 1=1.5, 2=2, 2=3, 4=4
int16_t afe44xx_CF1          = 5;     // feedback capacitor on Photodiode amplifier for LED1: 5pF, 5..275pF
int16_t afe44xx_RF1          = 500;   // Feedback resistor on Photodiode amplifier for LED1: 500kOhm, -1..1000kOhm, -1 = 0kOhm
uint8_t afe44xx_Fc           = 0;     // Low pass filter edge frequency 0=500Hz or 1=1000Hz
uint8_t afe44xx_CAmbient     = 0;     // Photodiode ambient current 0..9 micro Amp, you can measure by blocking the PD with black tape, depends on temperature
int8_t  afe44xx_stage2Gain2  = 0;     // stage 2 gain for LED 2, -1 disable, 0=1, 1=1.5, 2=2, 2=3, 4=4, its better to increase power of LED than to increase this gain
int16_t afe44xx_CF2          = 5;     // Feedback capacitor: 5pF 0..275 pF, same as LED1
int16_t afe44xx_RF2          = 500;   // Feedback resistor: 500kOhm -1..1000kOhm, same as LED1
/* Transmitter Stage */
uint8_t afe44xx_txRefVoltage = 0;     // Reference votlage for LEDs 1=0.5V, 0,2=0.75V, 3=1V, higher Voltage results in more current which increases brightness of LED
uint8_t afe44xx_range        = 0;     // Current range for LEDs 0=hig, 1=low, 2=high, 3=off // low is 50, 75, 100 mA, high 100, 150, 200 mA depending on voltage reference
uint8_t afe44xx_led1Power    = 24;    // LED1 power 0..255, this should be adjusted for each measurement subject so that readings are larger than 1,048,576 (half of max reading (2^21-1))
uint8_t afe44xx_led2Power    = 24;    // LED2 power 0..255
/* Digitial IO mode */
bool    afe44xx_tristate     = false; // Output logic tri state should be enabled if more than one SPI device is attached to the SPI bus, when the device is inactive to reduce power consumption
bool    afe44xx_hbridge      = true;  // use h-bridge for LED driver, this should be the default default
uint8_t afe44xx_alarmpins    = 0b101; // Photodiode and LED alarm pins can indicate activity, e.g. show that LED is sampled or LED is converted, see options below
/* 
Alarmpins
  PD Alarm pin                LED Alarm pin
  0 Sample LED2 pulse         Sample LED1 pulse
  1 LED2 LED pulse            LED1 LED pulse
  2 Sample LED2 ambient pulse Sample LED1 ambient pulse
  3 LED2 convert              LED1 convert
  4 LED2 ambient convert      LED1 ambient convert
  5 None                      None
  6 None                      None
  7 None                      None 
*/
float   afe44xx_factor       = 1.0; // Timing factor e.g. 0.5 or 8, 1 default, the default factor results in 500 samples per second.
/* 
Timing
  With a factor of 1.0 the default timing for 8000 clock cycles occurs. 
  At 4Mhz clock rate this will result in 500 measurements per second,
  on both red and ir channel including backgroudn subtraction.
  If averaging is set other than 1, the data rate will be reduced by the numer of averages.
  The default timing is taken from data sheet example. ADC reset pulse length is not changed by factor.
  If factor is <1 you will receive more samples per second, if its larger you will receive less samples per second.
  */
/* Hardware configuration*/
bool    afe44xx_bypassADC    = false; // use internal ADC, the default
bool    afe44xx_powerRX      = true;  // power the photodiode circuit, it will not work otherwise
bool    afe44xx_powerTX      = true;  // power the LED driver, it will not work otherwise
bool    afe44xx_powerAFE     = true;  // power the device, it will not work otherwise
uint8_t afe44xx_numAverage   = 4;     // number of averages caculated for LED1,2 and ambient measurements, this occurs inside the AFE
bool    afe44xx_running      = false; // keep track if system is running
bool    afe44xx_shortDiag    = true;  // short diagnostic 8ms or long diagnostics 16ms
bool    afe44xx_useXTAL      = true;  // use external crystal, otherwise provide clock signal, usual design is with crystal

// Program Globals
uint32_t   currentTime;                                               // Populated at beginning of main loop
uint32_t   lastTime;                                                  // to compute sampling frequency
float      samplingRate;                                              // computed in main loop
char       serialInputBuff[64];                                       // general text buffer
bool       serialCommandComplete = false;                             // keep track of serial input until we receive CR
const char waitmsg[] = {"Waiting 5 seconds, skip by sending enter"};  // Allows user to open serial terminal to observe the debug output before the loop starts
extern int currentLogLevel;                                           // log level when using the logger.cpp provided logging functions
char       tmpStr[256];                                               // general string buffer

// Data retrieved from the AFE
// ---------------------------
int32_t irRawValue = 0;      // raw value for IR LED data
int32_t redRawValue = 0;     // raw value for Red LED data
int32_t irAmbientValue = 0;  // Background reading for IR LED
int32_t redAmbientValue = 0; // Background reading for Red LED
int32_t irValue = 0;         // IR data, background subtracted by AFE
int32_t redValue = 0;        // Red data, background subtracted by AFE

// Instantiate the device driver
// -----------------------------
AFE44XX afe44xx(CS_PIN, PWDN_PIN, DRDY_PIN);

/******************************************************************************************************/
// Setup
/******************************************************************************************************/
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

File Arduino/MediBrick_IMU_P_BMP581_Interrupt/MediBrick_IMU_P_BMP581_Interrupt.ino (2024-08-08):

/*******************************************************************************
 * For the MediBrick IMU Board BMP581 Pressure Sensor Test
 * @author Urs Utzinger
 * @copyright GPLv3 
 ******************************************************************************/

#include <SPI.h>
#include "SparkFun_BMP581_Arduino_Library.h"
#include "logger.h"

// Create a new sensor object
BMP581 pressureSensor;

// SPI Settings
#define SCLK_PIN      SCK
#define MISO_PIN     MISO
#define MOSI_PIN     MOSI
// SPI Clock Frequency:
// EPS32: integer divisions of 80Mhz, e.g 80, 40, 20, 10, 5, 1
// BMP 851 3.3V max: 12MHz 1.8V max: 7MHz
// ICM 20948 1.8V max: 7MHz
// BSS138 level shifter, on delay 2.5, on rise 9, off delay 20ns, off fall 7ns = 40ns max transition for impulse: 25 MHz
#define SPI_SCLK_FREQUENCY 7000000 // 100 to 7000 kHz
#define UNUSED_CS_PIN   9
// IMU
#define ICM_CS_PIN     11
#define ICM_INT_PIN    13
// Pressure
#define BMP_CS_PIN      6
#define BMP_INT_PIN    12

int8_t err = BMP5_OK;

// OOR range specification. The center pressure is 1 atm (101325 Pa), and the
// window is the max value supported by the sensor (255)
// uint32_t oorCenter = 101325;
// uint8_t  oorWindow = 255;


// Flag to know when interrupts occur
volatile bool BMP_interruptOccurred = false;

void bmp581InterruptHandler() {
    BMP_interruptOccurred = true;
}

// -----------------------------------------------------------------------------

void setup() {

  // Chip Select pins
  // Set them high before setting output so that we have no transitions on the lines.
  // Do this first to make sure the sensors are not interrupted during power up
  digitalWrite(BMP_CS_PIN, HIGH); // deselect BMP chip
  digitalWrite(ICM_CS_PIN, HIGH); // deselect ICM chip
  digitalWrite(UNUSED_CS_PIN, HIGH); // deselect dummy chip
  pinMode(BMP_CS_PIN, OUTPUT);
  pinMode(ICM_CS_PIN, OUTPUT);
  pinMode(UNUSED_CS_PIN, OUTPUT);

  // Interrupt pins
  pinMode(BMP_INT_PIN, INPUT_PULLDOWN);
  pinMode(ICM_INT_PIN, INPUT_PULLDOWN);

  // Initialize the SPI library, use pin other than BMP_CS_PIN
  LOGI("Initialize SPI");
  SPI.begin(SCLK_PIN, MISO_PIN, MOSI_PIN, UNUSED_CS_PIN);

  // Initialize sensor and its SPI connection
  // If init fails it will attempt soft reset and init again
  err = pressureSensor.beginSPI(BMP_CS_PIN, SPI_SCLK_FREQUENCY);

    // logger
  currentLogLevel = LOG_LEVEL_INFO; // NONE, ERROR, WARN, INFO, DEBUG

  // Start serial 
  Serial.begin(500000);
  while (!Serial);

  // if Sensor startup was unsuccessfull report issue and try again
  // most common errors are illustrated, 
  while( err != BMP5_OK)
  {
    if (err == BMP5_E_NULL_PTR){
      LOGE("BMP581: driver not setup properly...");
    } else if (err == BMP5_E_COM_FAIL){
      LOGE("BMP581: communicationi failure...");
    } else if (err == BMP5_E_DEV_NOT_FOUND){
      LOGE("BMP581: device not found...");
    } else if (err == BMP5_E_INVALID_CHIP_ID){
      LOGE("BMP581: invalid chip id...");
    } else if (err == BMP5_E_POWER_UP){
      LOGE("BMP581: powerup check failure, NVM RDY is false or NVM ERR is true ...");
    } else if (err == BMP5_E_POR_SOFTRESET){
      LOGE("BMP581: soft reset failure...");
    } else if (err == BMP5_E_INVALID_POWERMODE) {
      LOGE("BMP581: invalid power mote...");    
    } else if (err == BMP5_E_INVALID_THRESHOLD) {
      LOGE("BMP581: invalid threshold...");    
    } else if (err == BMP5_E_FIFO_FRAME_EMPTY) {
      LOGE("BMP581: frame empty...");
    } else if (err == BMP5_E_NVM_INVALID_ADDR) {
      LOGE("BMP581: invalid NVM address...");
    } else if (err == BMP5_E_NVM_NOT_READY) {
      LOGE("BMP581: NVM not ready ...");
    } else if (err == BMP5_E_NVM_ERROR) {
      LOGE("BMP581: NVM error ...");
    } else { 
      LOGE("BMP581: Error: %d. Unexpected other failure, check datasheet...", err);
    }
    delay(500);
    err = pressureSensor.beginSPI(BMP_CS_PIN, SPI_SCLK_FREQUENCY);
  }

  LOGI("BMP581: connected!");

  // The BMP581 can sample up to 240Hz in normal mode.
  // BMP5_ODR_240_HZ  
  // BMP5_ODR_199_1_HZ
  // BMP5_ODR_160_HZ  
  // BMP5_ODR_140_HZ  
  // BMP5_ODR_120_HZ  
  // BMP5_ODR_100_2_HZ
  // BMP5_ODR_80_HZ 
  // BMP5_ODR_70_HZ 
  // BMP5_ODR_60_HZ 
  // BMP5_ODR_50_HZ 
  // BMP5_ODR_40_HZ 
  // BMP5_ODR_20_HZ 
  // BMP5_ODR_10_HZ 
  // BMP5_ODR_01_HZ 

  err = pressureSensor.setODRFrequency(BMP5_ODR_240_HZ);
  if( err != BMP5_OK) { LOGE("ODR setting failed! Error code: %d", err); }

  // The BMP581 can filter both the temperature and pressure measurements individually.
  // By default, both filter coefficients are set to 0 (no filtering). We can smooth
  // out the measurements by increasing the coefficients with this function
  // It appears the IIR length is proprtional to a reduction of sample rate
  // 3 Coefficients after a steap it takes 20 measurements to reach step
  // 127 coefficients it takes about 700 measurements to reach step 
  // BMP5_IIR_FILTER_BYPASS
  // BMP5_IIR_FILTER_COEFF_1 
  // BMP5_IIR_FILTER_COEFF_3   Fast, takes 2 previously measured data points and 2 previous filtered data points to compute current filtered data point
  // BMP5_IIR_FILTER_COEFF_7
  // BMP5_IIR_FILTER_COEFF_15 
  // BMP5_IIR_FILTER_COEFF_31 
  // BMP5_IIR_FILTER_COEFF_63 
  // BMP5_IIR_FILTER_COEFF_127 Most precise but slowest
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

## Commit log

2023-09-15 Thermistor Board
    [LTC2473CDR1.brd, LTC2473CDR1.sch]
2023-09-16 Thermistor Board
    Thermistor board with BOM and GERBER files for manufacturing and assembly
    [LTC2473CDR1-smt.csv, LTC2473CDR1.brd, LTC2473CDR1.sch, LTC2473CDR1_bom.xlsx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]
2023-09-16 Directory name
    [LTC2473CDR1-smt.csv, LTC2473CDR1.brd, LTC2473CDR1.sch, LTC2473CDR1_bom.xlsx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]
2023-09-17 Minor Updates LTC board
    Silkscreen
    Updates to via positions
    [LTC2473CDR1.brd]
2023-09-17 Skeleton for other boards
    [AD 2.brd, AD5933.sch, ECG.brd, ECG.sch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]
2023-10-25 Routing Impedance Board
2023-10-25 Impedance Circuit Explanation
    [Impedance.brd]
2023-11-06 ESP32 Continuous ADC
2023-12-10 Python Serial Helper
    First Release of Python Based Serial Interface emulating Arduino IDE.
2024-01-22 Example Arduino Code
    First release of example Arduino Code
    Updates to Impedance general design
2024-02-08 Board Updates, Reorganize
    [2_3.brd, 2_3.sch, AD 2.brd, AD5933.brd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]
2024-02-10 Updated SPO2
    Crosse Checked with Data Sheet and Evaluation Board
    Added 10Ohm resistors in data lines
    Adjusted capacitors
    [Impedance.brd, Impedance.sch, PulseOxi.brd, PulseOxi.sch]
2024-02-12 Impedance
    Minor change SPO2
    [Impedance.brd, Impedance.sch, PulseOxi.brd, PulseOxi.sch]
2024-02-12 Impedance Vref fic
    INA needs Vref
    [Impedance.brd, Impedance.sch]
2024-02-14 Impedance update
    [Impedance.brd, Impedance.sch]
2024-02-14 Merging project and Impedance update (description)
    [ECG.brd, ECG.sch, Galvanometer.brd, Galvanometer.sch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]
2024-02-22 BOM MAX30001G and board updates
    [Impedance_Potential.brd, Impedance_Potential.sch, Impedance_Potential_BOM.xlsx, Impedance_Potential_BOM_PCBManufacturer.xlsx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]
2024-02-23 CAM Impedance_Potential Board
    [Impedance_Potential-smt.csv, Impedance_Potential.brd, Impedance_Potential.csv, Impedance_Potential.sch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]
2024-02-24 3 Channel Analog Temp
    [Impedance_Potential.brd, PnP_Impedance_Potential_front.csv, PnP_Temp_front.csv, Temp.brd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]
2024-02-27 Temp
    3 Channel board
    Writeup update
    [Temp.brd, copper_top.gbr, drill_1_16.xln, gerber_job.gbrjob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]
2024-02-29 Sound Board
    Sound Board with ES8388 by PCBArtists
    Cleanup
    [AD8232_Heart_Rate_Monitor_v10.brd, AD8232_Heart_Rate_Monitor_v10.sch, ECG 7 by 7.brd, ECG 7 by 7.sch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]
2024-03-01 Updated Sound Board
    [Sound.brd, copper_bottom.gbr, copper_top.gbr, drill_1_16.xln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]
2024-03-05 Cleanup, organization and updates
    [AD8232_Heart_Rate_Monitor_v10.brd, AD8232_Heart_Rate_Monitor_v10.sch, ECG 7 by 7.brd, ECG 7 by 7.sch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]
2024-03-16 Board Updates
    All LEDs at same location
    Separated analog and digital ground
    Updated impedance components
    [ECG 7 by 7.brd, ECG 7 by 7.csv, Impedance.brd, Impedance.csv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]
2024-03-24 Board Updates
    Updated routing
    Updated silk labeling
    Sound board with ES8388 included
    Impedance and ECG board
    Working on IMU board
    Working on Environmental Airquality board
    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
    [ECG 7 by 7.brd, Impedance.brd, Impedance.csv, Impedance.sch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]
2024-03-30 Air quality
    [Airquality.brd, Airquality.csv, Airquality.sch, MICS6814 Sesnsing Resistors.xlsx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]
2024-04-02 Air Quality at 3.3V with 5V boost for PM sensor
    [Airquality.brd, Airquality.csv, Airquality.sch, copper_bottom.gbr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]
2024-04-21 IMU board
    Completed IMU board design
    Updated designs with ground via close to any other via.
    [AD8232_Heart_Rate_Monitor_v10.brd, AD8232_Heart_Rate_Monitor_v10.sch, Airquality.brd, IMU.brd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]
2024-05-02 Production Updates
    [Air_Quality_BOM.xlsx, Air_Quality_BOM_minimal.xlsx, Air_Quality_PnP.xlsx, Airquality.brd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]
2024-05-02 Sound Board Updates
    [Sound.brd, Sound.csv, Sound.sch, Sound_BOM.xlsx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]
2024-07-02 Merging Production Status to Github, Obtaining senior design files
    [Air_Quality_PnP.xlsx, Airquality.brd, ECG.brd, ECG.sch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]
2024-08-08 Passed Tests
    Many sensors passed testing,
    Many library updates
    [Airquality.sch, IMU.brd, IMU.sch, Steinhart-Hart inverse fit.ods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]
2024-08-11 Docu Updates
    [Hemoglobin Data.ods]
2024-08-14 Mechanical Designs, Documentation
    [Board.stl, Face Plate - IMU.stl, Face Plate - Plain.stl, MicroController and Battery.stl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]
2024-10-18 Major Update
    [Airquality.brd, Airquality.sch, Board.stl, Face Plate - BioZ.stl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]
2024-10-18 Documentation Updates
    [Part 100540.SLDPRT, Part 100540.STL]
2024-10-19 Updated documentation
    [PulseOxi_BOM.xls, PulseOxi_BOM.xlsx]
2024-10-19 PCBWay quotations
    [T-1Y10W735621A-2sets-PulseOxi_BOM_noDB9(2024-05-01).xls, T-1Y19W735621A-2sets-Sound_BOM(2024-08-22).xls, T-1Y4W735621A-2sets-Air_Quality_BOM_minimal(2024-04-29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]

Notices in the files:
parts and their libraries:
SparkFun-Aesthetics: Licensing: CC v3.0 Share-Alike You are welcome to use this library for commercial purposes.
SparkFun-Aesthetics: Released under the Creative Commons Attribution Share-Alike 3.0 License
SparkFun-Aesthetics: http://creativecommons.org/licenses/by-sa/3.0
